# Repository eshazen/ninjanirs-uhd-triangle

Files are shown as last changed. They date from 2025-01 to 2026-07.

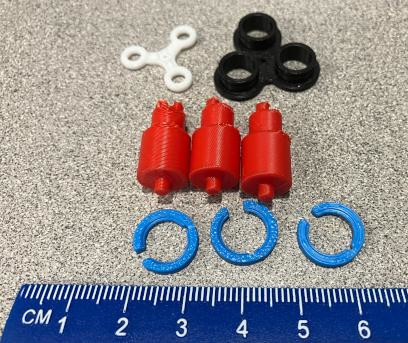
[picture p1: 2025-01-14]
milestone_prototype/parts_photo.jpg

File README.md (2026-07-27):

# ninjanirs-uhd-triangle

### 2026-07-27

Printing 10 pcs `...onshape/UHD_Assembly_Filled_2026-07-13.stl` with .08mm extra fine.

(the other ones are still in the car)

### 2026-07-13

Printing `...onshape/UHD_Assembly_Filled_2026-07-13.stl` with .08mm extra fine.

40m time.

David wants 25 pcs.

### 2026-06-04

Printing UHD_Assembly_Filled
<br>This version has a "hull" shape around the optodes for (much) faster printing and no support headaches

Orient with light pipes facing up, tree support
<br>Two versions:  Standard, and 0.08mm fine

### 2026-05-06

Now working on solid triad for "production" for mechanical test.
<br>See `UHD_Assembly_Filled` in onshape.  Needs a new sketch which
defines a convex hull around the optode features to fill in the body.
Also need to fill the volume below the springtop with a pyramid-like
solid.

Really we need an algorithm which would traverse a range of Z and
generate a 3D hull formed by a 2D hull at each Z.

### 2026-03-20

* Printing second springtop (still 1-up).
<br>Printed two groups of 3 so total (8) pieces now (1 fail so 7 total)
* Printing (4) grommets with brim (2:14)  OK.

### 2026-03-18

Starting production print (some R&D first).
<br>Printing UHD_Assembly_Ver1 as is using 0.4mm nozzle
and profile "0.08mm Extra Fine".  Quoted time 42m.
<br>_If this doesn't work we'll change to 0.2mm nozzle._

Seems OK.  Printing Grommets with same settings.
Also seems ok with some cleanup.

Printing springtop both ways up, same settings.  Broke both but
right-side up seems best if we can manage to get it off the support.
<br>Trying again right-side up.  OK with care

Printing caps with same settings (right-side up).
<br>Caps don't quite fit in springtop.

#### Re-printing all with 0.2mm nozzle

* Printing grommets using "0.06mm High Quality".  Time est 38min
<br>Fails with non-adhered parts

Make some changes as AI suggests:

* Change first layer height to 0.16mm.
* Change bed temp from 55 to 60 for both first and subsequent layers
* Change initial layer speed to 20mm/s
  <br>(in Filament profile)

Did not (yet) try to scrub the plate with dish soap!

Print the grommets again, much better.

Now the optodes, same settings.  Est 1:07.  Ok.

And the caps.  45min.  OK

Springtop:  enlarge hole to 3.75 and drill through the arms.  26m
<br>Print failed (bad adhesion).  Cleaned plate and tried again.  Fail
<br>Change to "0.12mm Standard" and added one layer of raft.  Fail.

Probably need to print these with 0.5mm nozzle?  Or somehow create a raft?
<br>Or possibly it's the white filament?

Reset bed temp to 55 per Steve's suggestion.
<br>Clean bed with Dawn soap.  Add a brim.  Try again.  Success!

    Process -> objects -> Others -> Brim type "Outer brim"

Springtop now fits OK.

### 2025-11-23

Re-starting project.  Opened UHD_Assembly_Ver1 on Onshape.
The groove depth 0.75 was missing, add it somewhat arbitrarily.

<pre>
   1.9
+--------+
|        |
|        |
|        |
|     .75|
|    +---+ 
|    |     0.57
|    +---+ 
|        | 0.5
+--------+
</pre>

Attempting to print with 0.2mm nozzle, preset
<br>0.06mm High Quality @BBL X1C 0.2 nozzle
<br>Rotate so attach peg is up on build plate
<br>This is a 37m print for one, with support

Fix the slot, print again with "Tree Slim" support,
right-side up this time.

<pre>
   1.9
+--------+
|        |
|        |
|        |
|     .3 |
|    +---+ 
|    |     1
|    +---+ 
|        | 0.5
+--------+
</pre>

This seems better.  Also printed a copy of `test_pegs` and a set of optodes.

## 2025-06-10

Working on attachment to ninjaCap.  Trying some small retaining rings
from McMaster:

| Item | P/N       | OD    | Groove wid | Groove dia |
|------|-----------|-------|------------|------------|
| 1    | 98410A111 | 1/8"  | .012"      | .117"      |
| 2    | 98410A815 | 5/32" | .012"      | .146"      |
| 3    | 98410A110 | 3/16" | .018"      | .175"      |

Printing a test peg for number 3 (A110)

* Peg dia = 0.177
* groove wid = 0.018
* grove dia = 0.168

Using 0.2mm nozzle
<br>Profile "0.06mm High Quality @BBL X1C 0.2 nozzle"

Fits nicely, but clip probably not wide enough to secure to flexible
cap.  Maybe a plastic or metal washer under the clip?

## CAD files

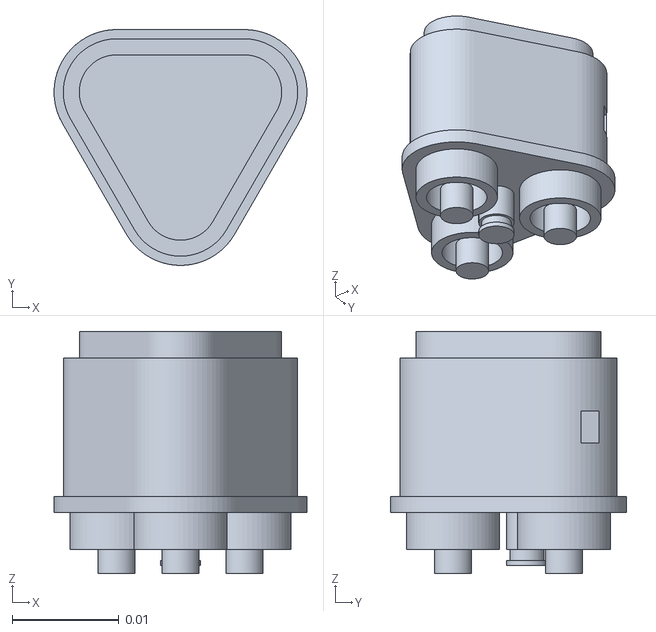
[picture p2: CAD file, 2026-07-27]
milestone_prototype/onshape/UHD_Assembly_Filled_2026-07-13.stl
0.0237 x 0.0221 x 0.0227

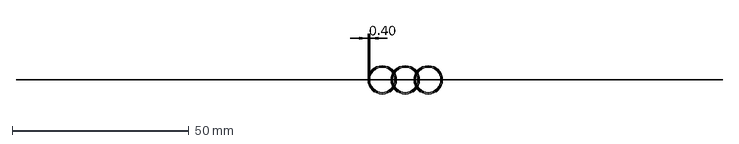
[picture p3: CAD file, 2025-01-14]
milestone_prototype/#triple_sensor-patch_assembly_v7_cs.dxf
0.40

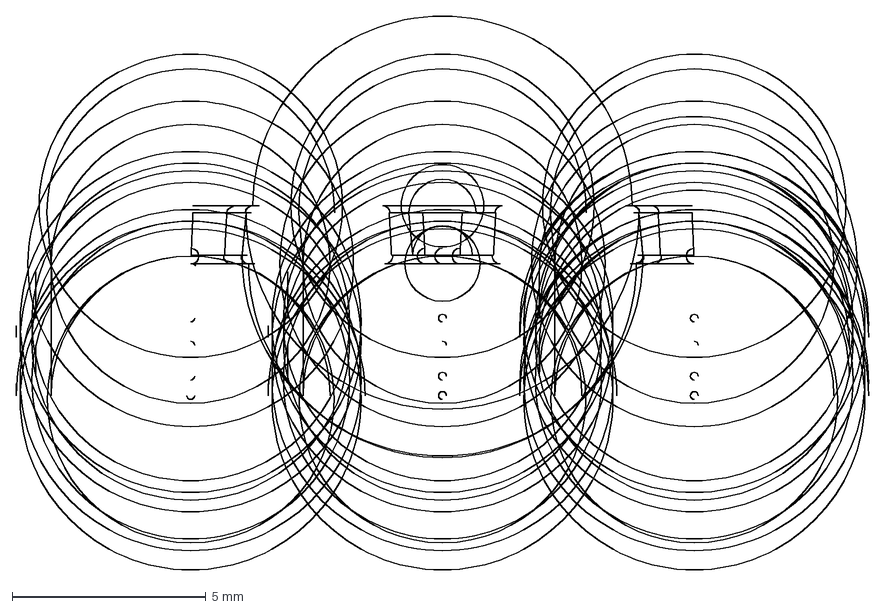
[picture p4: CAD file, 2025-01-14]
milestone_prototype/triple_sensor-patch_assembly v7grommet v9.dxf
22.0 x 14.3 mm

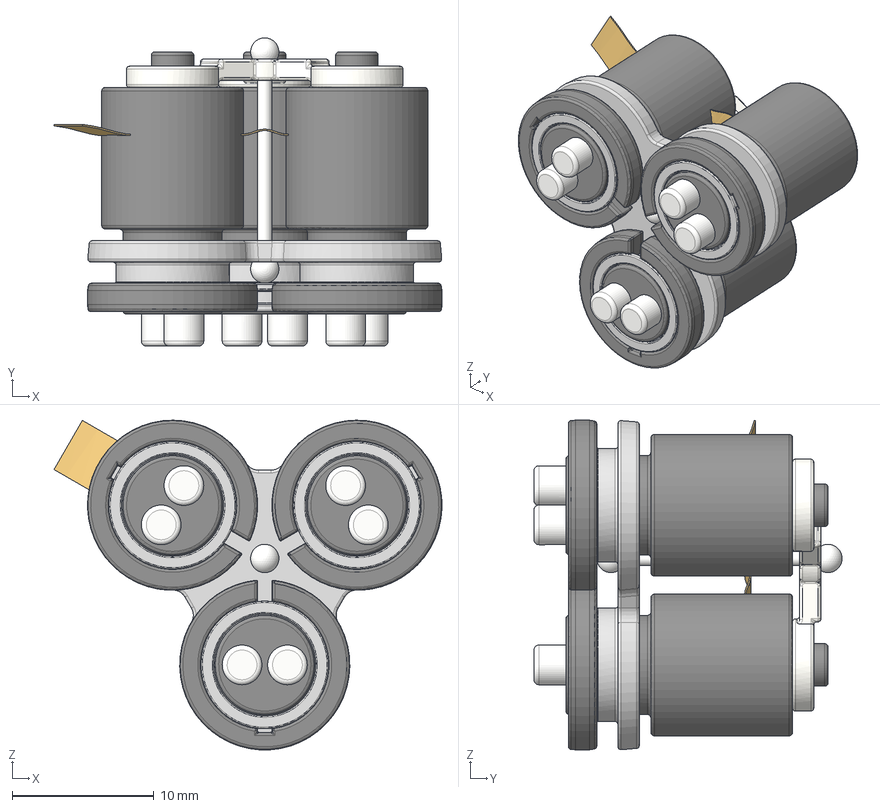
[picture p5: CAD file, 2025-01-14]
milestone_prototype/patch_assembly v7.step
27.4 x 21.7 x 23.2 mm
optode x 3
grommet
RubberString
springtop
clip x 3
PCB12 x 2
PCBMain

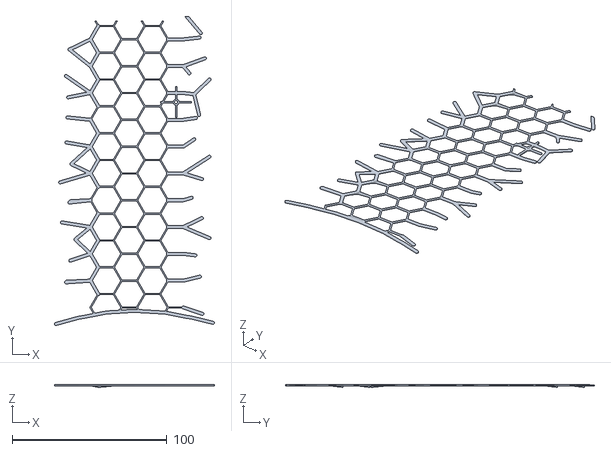
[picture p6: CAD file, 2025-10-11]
60_UHD/top1_proc.stl
103.4 x 199.6 x 1.90

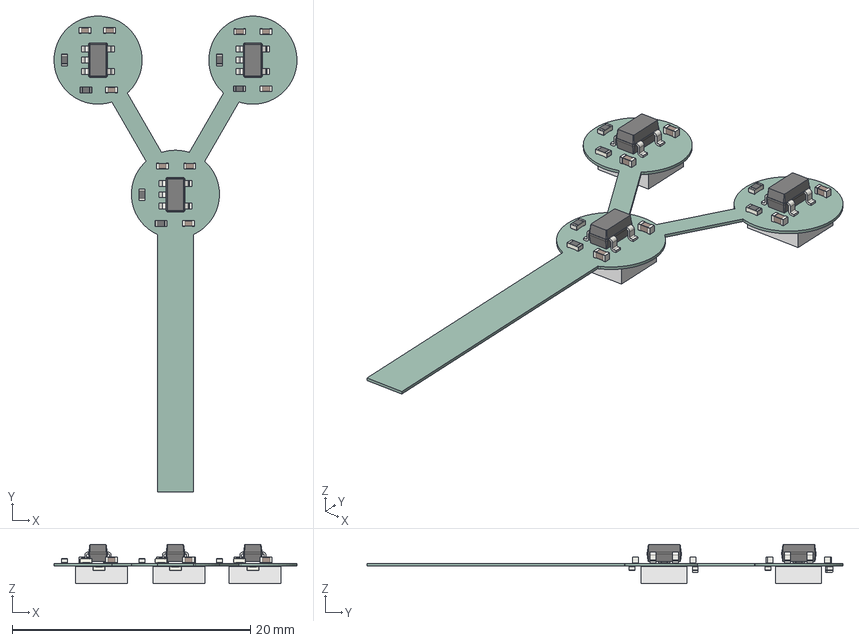
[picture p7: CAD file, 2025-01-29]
KiCAD/extra_4mm/hpk_5mm.step
20.4 x 40.0 x 3.30 mm
R_0402_1005Metric x 12
C_0402_1005Metric x 12
SOT_23_5 x 3
_autosave-hpk_5mm_PCB

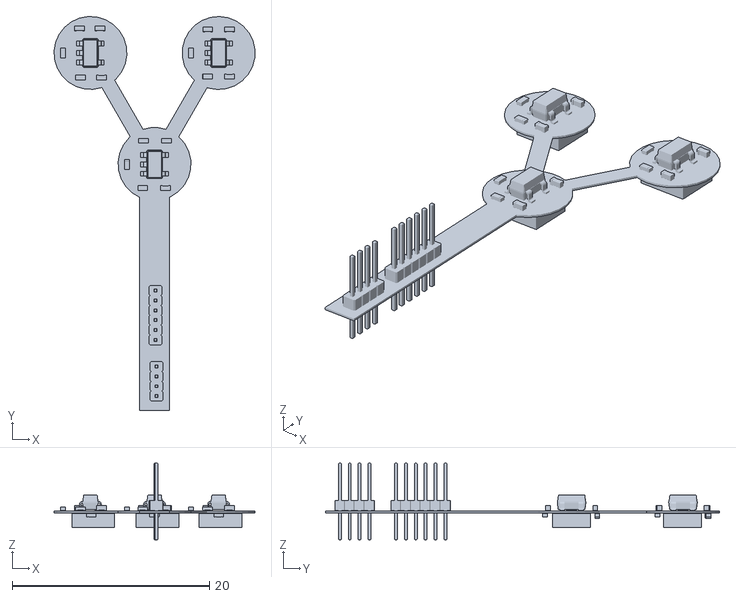
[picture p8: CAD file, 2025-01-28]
KiCAD/hpk_5mm/Unnamed-hpk_5mm 1.stl
20.4 x 40.0 x 7.80

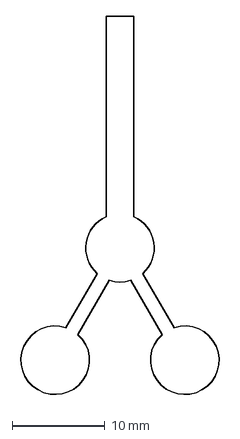
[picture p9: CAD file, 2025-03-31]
mech/first_flex_triangl_1mm.dxf
22.3 x 41.3 mm

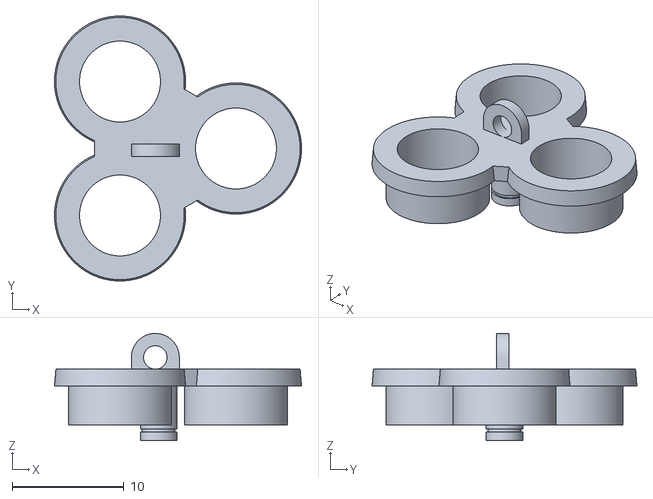
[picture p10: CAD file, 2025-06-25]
milestone_prototype/my_3d/print/grommet_1.stl
22.1 x 23.7 x 9.60

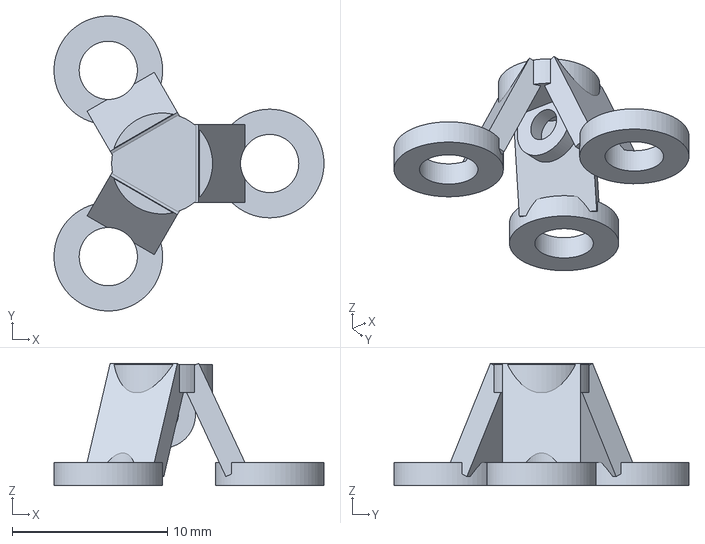
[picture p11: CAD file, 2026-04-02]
milestone_prototype/my_3d/print_2026/Grommets.3mf
17.4 x 19.0 x 7.88 mm

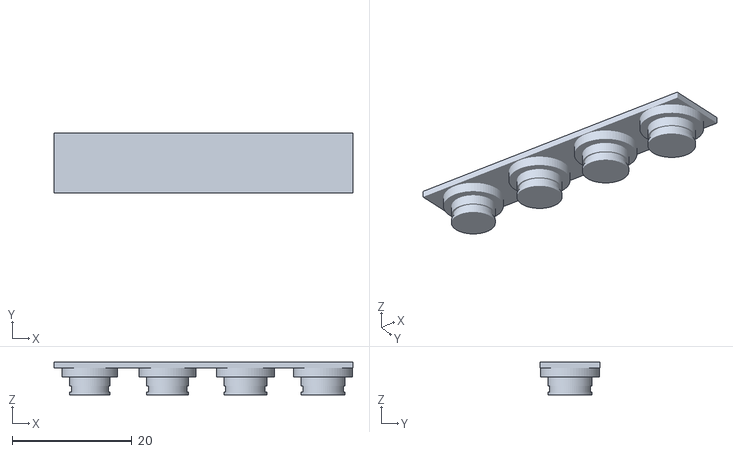
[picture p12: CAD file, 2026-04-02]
milestone_prototype/my_3d/test_source_pegs.stl
50.0 x 10.0 x 5.50

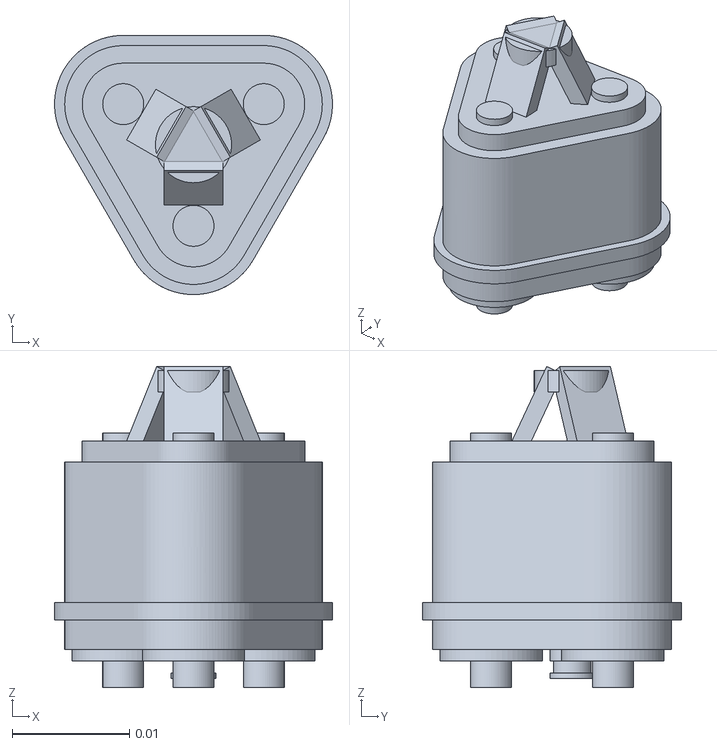
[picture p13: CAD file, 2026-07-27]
milestone_prototype/onshape/Solid_Triad.stl
0.0237 x 0.0221 x 0.0274

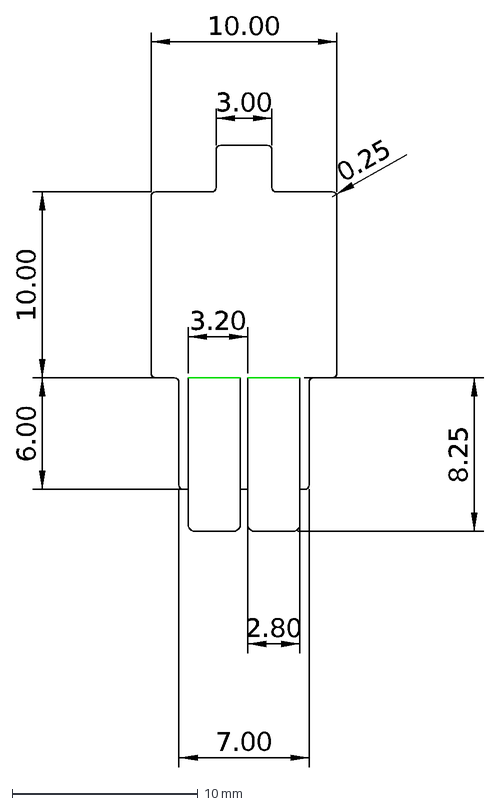
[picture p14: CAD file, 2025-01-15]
milestone_prototype/optode_v006_cs001.dxf
10.00
3.00
2.80
7.00
8.25
0.25
3.20
6.00

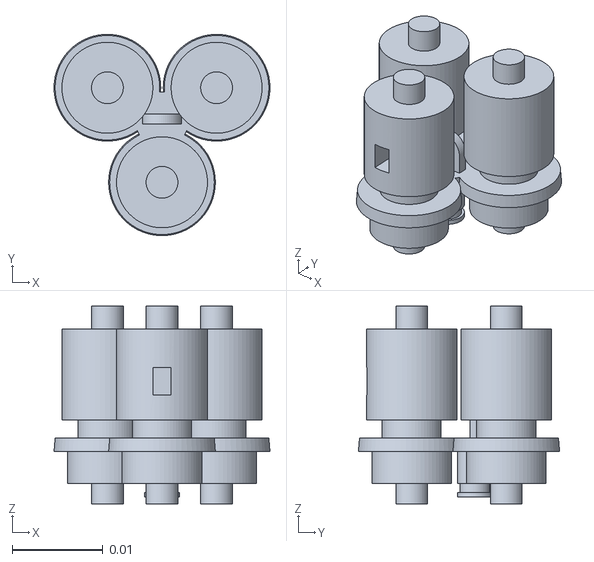
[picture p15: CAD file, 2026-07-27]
milestone_prototype/solid_triode/SolidTriode.stl
0.0237 x 0.0221 x 0.0217

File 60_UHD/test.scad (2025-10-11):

$fn = 32;

import("sideLeft_proc.stl");
//translate( [122.13, 118.27, 0])
//color("red") {
//  difference() {
//    cylinder( d=5, h=1.3);
//    translate( [0, 0, -1])
//      cylinder( d=3.5, h=3);
//  }
//}
//

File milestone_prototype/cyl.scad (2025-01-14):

$fn=64;
e = 0.1;

dia = 6;
wall = 0.5;
hgt = 10;

difference() {
  cylinder( h=hgt, d=dia);
  translate( [0, 0, -e])
    cylinder( h=hgt+2*e, d=dia-2*wall);
}

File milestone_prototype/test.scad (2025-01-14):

$fn=64;
import("triple_grommet.stl");

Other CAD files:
UHD_60cm/top1_proc.stl
60_UHD/right_fix.stl
mech/first_flex_triangl_4mm.dxf
milestone_prototype/clips_3.dxf
KiCAD/extra_4mm/test.scad
60_UHD/top2_proc.stl
KiCAD/extra_4mm/hpk_5mm.3mf
KiCAD/extra_4mm/hpk_5mm.stl
KiCAD/extra_4mm/models/si13360-3050pe-cube.step
KiCAD/extra_4mm/models/si13360-3050pe.scad
UHD_60cm/top2_proc.stl
mech/first_flex_triangle.dxf
milestone_prototype/cyl.stl
milestone_prototype/my_3d/98410A110_External Retaining Ring.STEP
milestone_prototype/my_3d/98410A110_Ring.stl
milestone_prototype/my_3d/98410A111_External Retaining Ring.STEP
milestone_prototype/my_3d/98410A111_Ring.stl
milestone_prototype/my_3d/cap.scad
milestone_prototype/my_3d/cap/98410A110_Ring.stl
milestone_prototype/my_3d/cap_1.3mf
milestone_prototype/my_3d/cap_1.stl
milestone_prototype/my_3d/cap_2.stl
milestone_prototype/my_3d/flexi.3mf
milestone_prototype/my_3d/geom.scad
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

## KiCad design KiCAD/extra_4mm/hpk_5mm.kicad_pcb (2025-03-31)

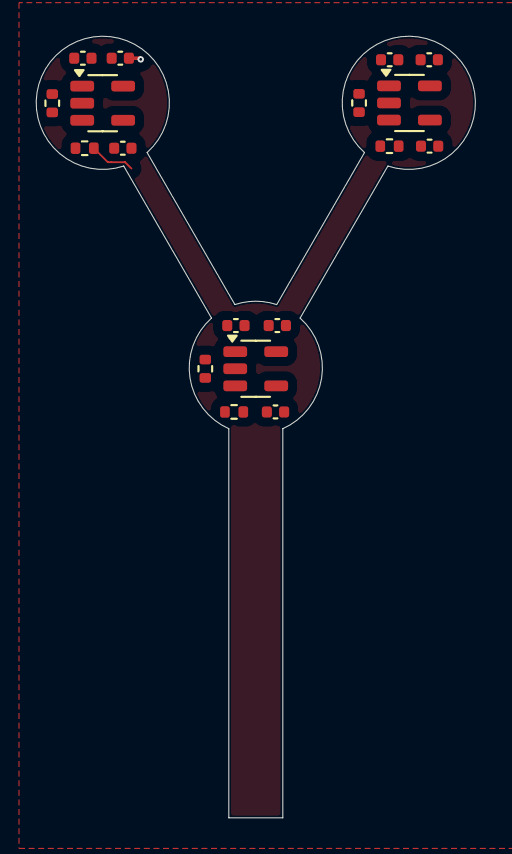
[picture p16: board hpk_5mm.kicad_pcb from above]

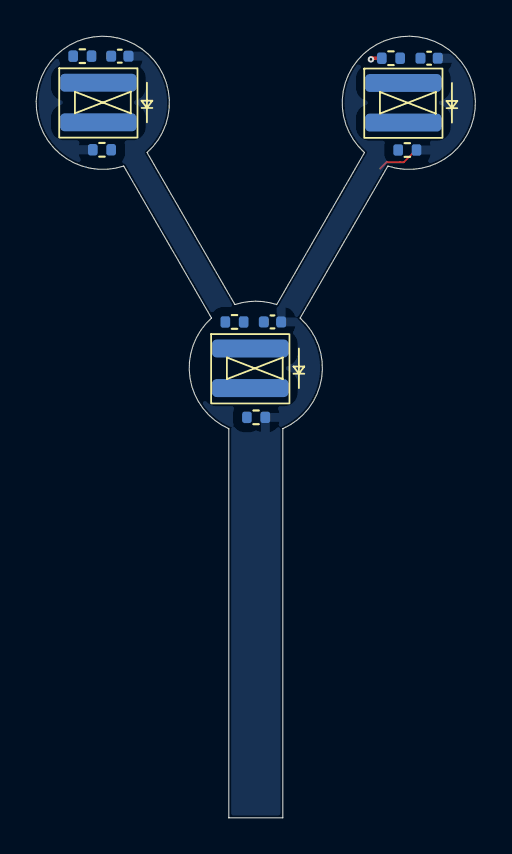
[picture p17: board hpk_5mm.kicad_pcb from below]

Board: 2 copper layers, 24.4 x 43.4 mm, 30 parts (12 on the bottom side), 13 nets.

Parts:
C1, C2, C3, C4, C5, C6, C7, C8, C9, C10, C11, C12: 0.1uF; C_0402_1005Metric
D1, D2, D3: S13360-3050PE; s13360-3050pe
R1, R2, R3, R4, R5, R6, R7, R8, R9, R10, R11, R12: 1k; R_0402_1005Metric
U1, U2, U3: OPA810xDBV; SOT-23-5

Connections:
/sipm_tia1/V+: C2.1, C6.1, C10.1, U1.5 (V+), U2.5 (V+), U3.5 (V+)
/sipm_tia1/V-: C4.1, C8.1, C12.1, U1.2 (V-), U2.2 (V-), U3.2 (V-)
/sipm_tia1/VBIAS: R1.1, R5.1, R9.1
GND: C1.2, C2.2, C4.2, C5.2, C6.2, C8.2, C9.2, C10.2, C12.2, R2.1, R6.1, R10.1, U1.3 (+), U2.3 (+), U3.3 (+)
unnamed: C3.2, R3.2, R4.1, U1.1
unnamed: C7.2, R7.2, R8.1, U2.1
unnamed: C11.2, R11.2, R12.1, U3.1
unnamed: C3.1, D1.2 (A), R2.2, R3.1, U1.4 (-)
unnamed: C1.1, D1.1 (K), R1.2
unnamed: C7.1, D2.2 (A), R6.2, R7.1, U2.4 (-)
unnamed: C5.1, D2.1 (K), R5.2
unnamed: C11.1, D3.2 (A), R10.2, R11.1, U3.4 (-)
unnamed: C9.1, D3.1 (K), R9.2

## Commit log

2025-01-14 3D stuff to print
    [#triple_sensor-patch_assembly_v7_cs.dxf, clips_3.dxf, cyl.scad, cyl.stl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]
2025-01-15 3D design
    [grommet.scad, optode-Fillet006.stl, optode.FCStd, optode.scad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]
2025-01-15 new 3D model with spring
    [grommet.scad, grommets.3mf, optode.3mf, patch.scad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]
2025-01-21 ready to print 3X model with reinforced spring attach
    [grommets.3mf, optode-Fillet006.stl, optode.3mf, parts_print_3x.3mf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]
2025-01-26 working on hollow optode and HPK SiPM
    [hpk_5mm.kicad_pcb, hpk_5mm.kicad_sch, optode_hollow.scad, patch.scad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]
2025-01-27 adding TIA for test layout
    [hpk_5mm.kicad_sch]
2025-01-28 trial 3-channel flexi
    [Unnamed-hpk_5mm 1.stl, first_flex_triangle.dxf, hpk_5mm.3mf, hpk_5mm.kicad_pcb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]
2025-01-29 flexi design
    [flexi.3mf, grommet.3mf, hpk_5mm.kicad_pcb, hpk_5mm.kicad_sch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]
2025-02-27 tweaking for 3d print at home
    [grommet.3mf, grommet.scad, grommet_7.25.3mf, grommet_7.5.3mf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]
2025-02-27 reduce size of spring attach
    [grommet.3mf, patch.scad, spring.scad]
2025-03-31 flex protots
    [first_flex_triangl_1mm.dxf, first_flex_triangl_4mm.dxf, grommet.3mf, hpk_5mm-B_Cu.gbr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]
2025-05-02 tweaking hollow optodes
    [optode_hollow.scad, patch.scad]
2025-05-02 prep for new prints
    [caps_1X.3mf, caps_3x.3mf, flexi_3x.3mf, grommets_1X.3mf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]
2025-05-05 working on optode
    [grommets_1X.3mf, optode_1X.3mf, optode_group_1X.3mf, optode_hollow.scad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]
2025-05-05 move optode floor up and fix slots to match
    [optode_group_1X.3mf, optode_hollow.scad, patch.scad]
2025-05-06 tweak settings for printing
    [caps_1X.3mf, grommets_1X.3mf, optode_1X.3mf, optode_group_1X.3mf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]
2025-05-29 As built with 13mm spacing for NIRX demo
    [98410A110_External Retaining Ring.STEP, cap_3X.3mf, caps.stl, caps_3x.3mf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]
2025-05-29 Change to 12mm pitch and add retainer clip
    [98410A110_Ring.stl, grommet.scad, patch.scad, springtop.scad]
2025-06-11 working on packing/cap
    [98410A111_External Retaining Ring.STEP, 98410A111_Ring.stl, cap.scad, cap_3X.3mf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]
2025-06-11 add cap option
    [98410A110_Ring.stl, cap_1.3mf, cap_1.stl, patch.scad]
2025-06-16 tweaking optode
    [cap.scad, cap_2.stl, optode_hollow.scad, patch.scad]
2025-06-16 adjust patch geometry
    [cap.scad, grommet.scad, patch.scad]
2025-06-17 working on DB new lattice options
    [cap.scad, geom.scad, grommet.scad, hex.scad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]
2025-06-18 working on new hex
    [hex.scad, newhex.scad]
2025-06-18 new hex
    [grommet.scad, newhex.scad, patch.scad, springtop.scad]
2025-06-18 hex ok, missing source optode grommet mount
    [grommet.scad, newhex.scad, patch.scad]
2025-06-24 small tweaks
    [optode_hollow.scad, patch.scad]
2025-06-24 new lattice
    [newerhex.scad]
2025-06-25 David's new lattice
    [grommet.scad, grommet_1.stl, newerhex.scad]
2025-06-25 refining new hex
    [grommet.scad, grommet.stl, grommet2.stl, newerhex.scad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]
2025-06-30 working on test peg
    [newerhex.scad, test_pegs.scad]
2025-10-11 add SK first try
    [Grommets.stl, Optode_Triad.stl, Optode_Triad_Grommets.3mf, grommet.scad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]
2026-03-18 lots of updates, including 'final' printables
    [Grommets.stl, Optode_Triad.stl, caps.stl, newerhex.dxf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]
2026-03-19 README. Springtop print fails
2026-03-24 reduce cap height from 4.5 to 3
    [optode_hollow.scad, patch.scad]
2026-04-02 as printed
    [Grommets.3mf, caps_sm.stl, caps_sm_3sets.3mf, patch.scad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]
